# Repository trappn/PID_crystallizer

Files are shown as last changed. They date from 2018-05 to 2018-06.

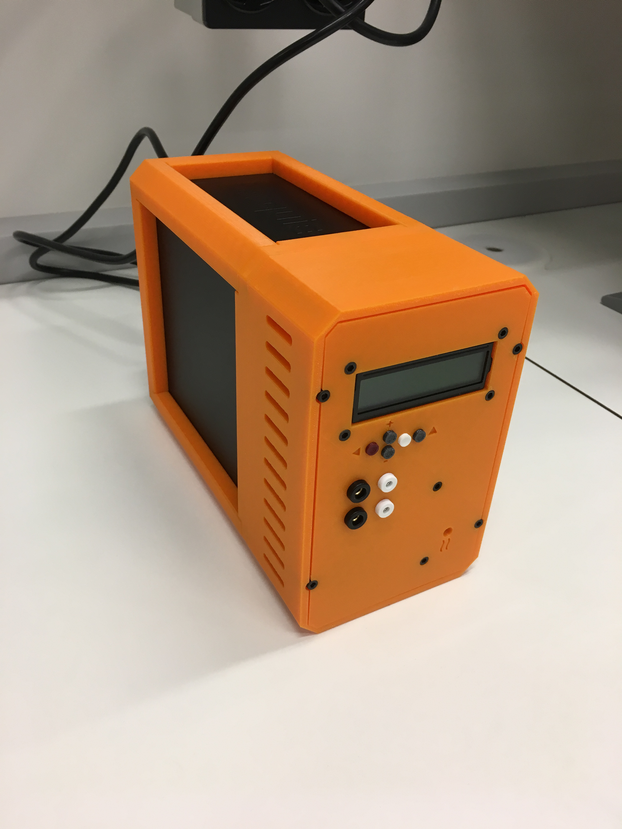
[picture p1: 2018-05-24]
photos/assembled_unit.JPG

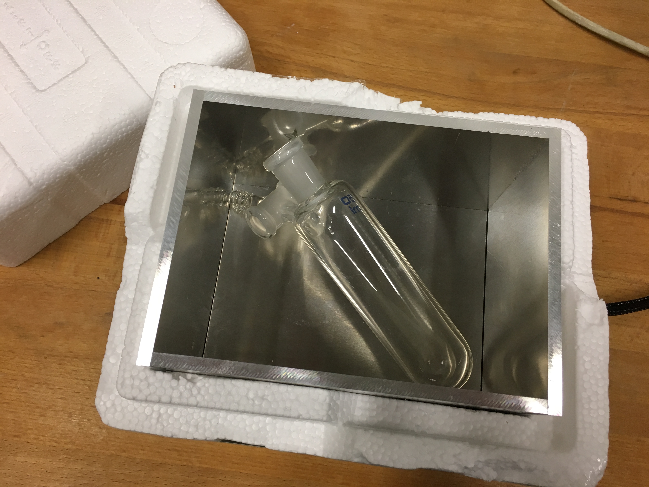
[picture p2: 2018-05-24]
photos/lowtemp_box_2.JPG

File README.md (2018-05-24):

# PID_crystallizer
Arduino-based programmable ramping PID controller 
<p>
Crystalheater Controller<br>
(c) N. Trapp @ Small Molecule Crystallography Center<br>
ETH Zürich, 2018<br>
</p>
<p>  
derived from:<br>
"Sous Vide Controller", (c) Bill Earl - for Adafruit Industries<br>
based on Arduino PID and PID AutoTune Libs, (c) Brett Beauregard<br>
</p>
<p>
 Used libraries: PID_v1.h, PID_AutoTune_v0.h, Wire.h, Adafruit_RGBLCDShield.h, SmoothThermistor.h, EEPROM.h
</p>
<p>
<ul>
  <li>designed around Arduino Uno with Robotdyn RGB 16x2 keypad shield, 100K NTC thermistor, standard DC/DC SSD and any 12V DC heating element</li>
  <li>minimized assembly time with ATX PSU & 3D printed case</li>
  <li>4 profiles for ramping (linear, oscillate, steps, sawtooth)</li>
  <li>uses PID autotuning (only necessary once for a specific heater setup) or manually set PID parameters</li>
  <li>can heat or cool</li>
  <li>logging via USB serial</li>
  <li>external wire harness allows placing heater box in fridge for cooling below RT</li>
  <li>stores settings in EEPROM</li>
  <li>projected runtime is displayed when changing settings</li>
  <li>thermistor safety: switches off when sensor shorts, breaks or is unplugged</li>
  <li>make sure to adjust Tmax (default:60) & Tmin (default:-40) in the sketch to safe values for your heater setup before compiling!</li>
  <li>extensive testing has shown long-term stability (>2 weeks) and accuracy (+/-0.1°C)</li>
</ul>
</p>

Usage:<br>
<table style="">
  
  <tr>
   <td>right</td><td>start or next</td>
  </tr>
  <tr>   
   <td>left</td><td>stop or previous, during ramping: stop and hold current temp</td>
  </tr>
  <tr>
   <td>up/down</td><td>during ramping&heating: show info screens</td>
  </tr>
  <tr>
   <td>shift</td><td>hold for larger increments in settings</td>
  </tr>
  <tr>
   <td>shift & +</td><td>start autotune (temp must be within 1°C of setpoint)</td>
  </tr>
  <tr>
   <td>shift & -</td><td>PID parameter settings</td>
  </tr>
  <tr>
   <td>shift & right</td><td>start ramp</td>
  </tr>
</table>

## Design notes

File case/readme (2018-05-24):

USBcover.scad contains only a simple plug (I drilled a 28mm hole in the case side to access the USB port for logging).

case structural parts (credits to alebrescia): https://www.thingiverse.com/thing:2321751
case faceplate & buttons: https://www.thingiverse.com/thing:2791368
heater box mold: https://www.thingiverse.com/thing:2891015
vial holders: https://www.thingiverse.com/thing:2891050

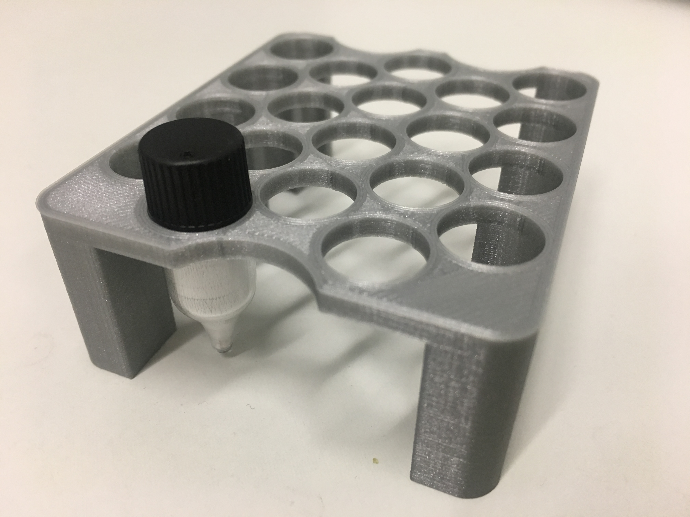
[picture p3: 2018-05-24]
photos/vialholder_small.JPG

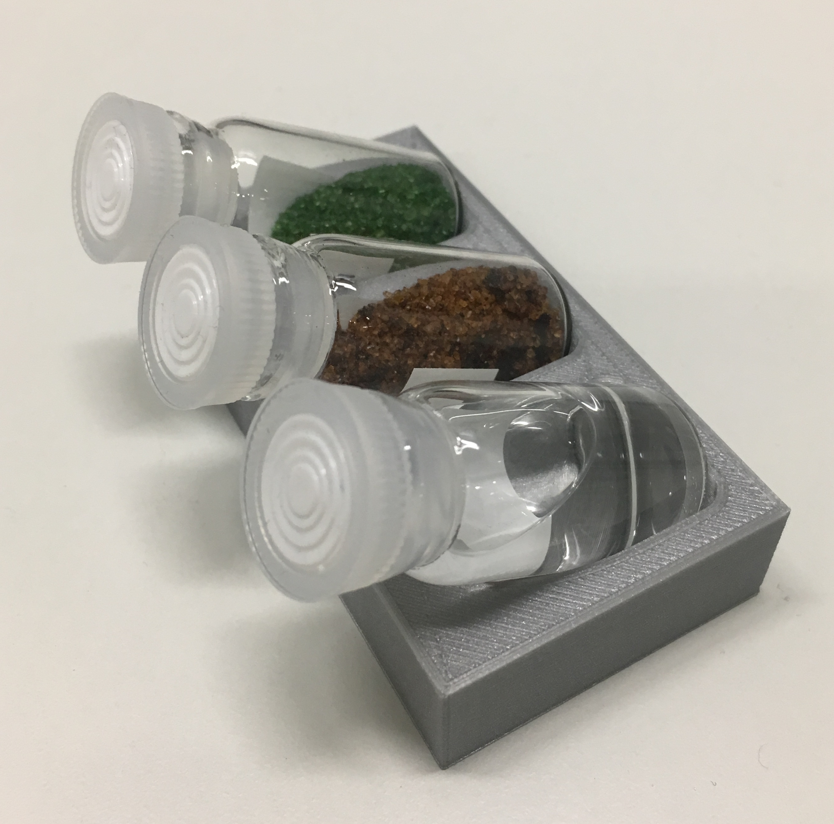
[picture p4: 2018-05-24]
photos/vialholder_large.JPG

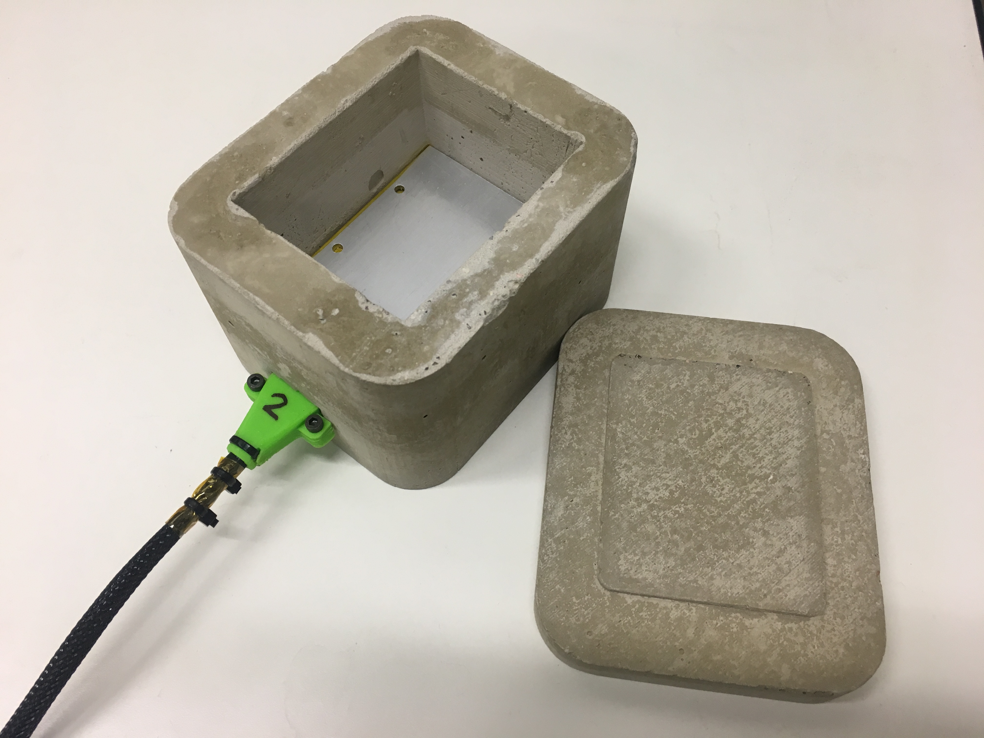
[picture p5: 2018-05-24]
photos/hightemp_box.JPG

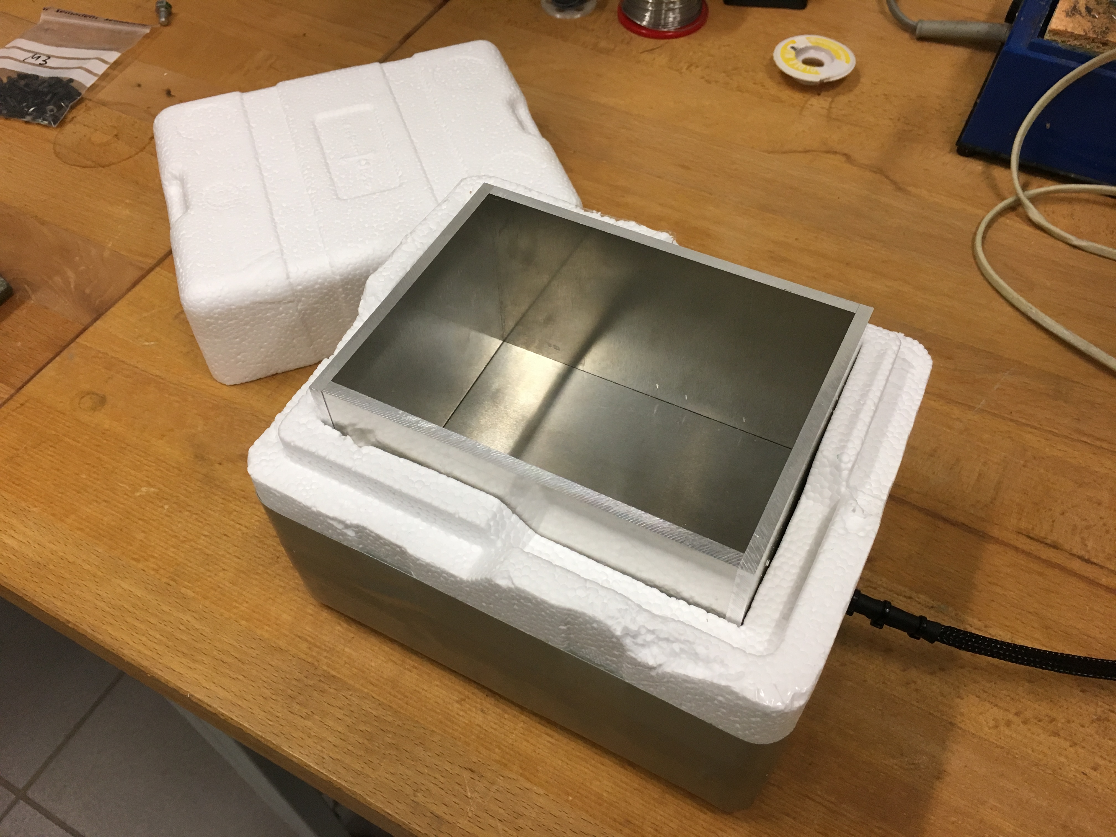
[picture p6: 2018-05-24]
photos/lowtemp_box_1.JPG

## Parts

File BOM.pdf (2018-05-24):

Part | Source (example) Link / Order No. (example) | Pack Unit Price (CHF) needed (# or m) Price total (CHF)

Electronics
ATX Power Supply >200W | scrap | | 1 | 0 | 1 | 0.00
Arduino UNO R3 clone | Aliexpress | https://www.aliexpress.com/item/high-quality-One-set-UNO-R3-MEGA328P-CH340G-For-Arduino-UNO-R3-Original-Chip-16Mhz/32833268761.html | 1 | 3.26 | 1 | 3.26
RGB LCD Shield with Keypad | Aliexpress | https://www.aliexpress.com/item/LCD-RGB-16x2-keypad-Buzzer-Shield-for-Arduino-LCD-RGB-1602/32812502875.html | 1 | 11.18 | 1 | 11.18
Solid State Relay DC-DC | Aliexpress | https://www.aliexpress.com/item/IMC-hot-New-Plastic-Metal-Solid-State-Relay-SSR-DC-DC-25A-3-32VDC-5-60VDC/32798514191.html | 1 | 4.07 | 1 | 4.07
Wires
Resistor 100kOhm | Aliexpress | https://www.aliexpress.com/item/100pcs-1-4W-1R-2-2M-1-Metal-film-resistor-series-100R-220R-1K-1-5K/32847096736.html | 100 | 0.66 | 1 | 0.01
Lab Jack Socket 2mm | | | | | 2
Lab Jack Socket 4mm | | | | | 2

Heater
Heater Element | | https://www.aliexpress.com/item/1PCS-PTC-Thermostat-Aluminum-Heating-Element-Heater-Plate-60W-AC-DC-12V-180-Degree-Incubator-Dehumidification/32812440130.html | 1 | 4.81 | 1 | 4.81
NTC Thermistor (100K, long wire) | Aliexpress | https://www.aliexpress.com/item/5Pcs-lot-100K-ohm-NTC-3950-Thermistors-with-cable-for-3D-Printer-Reprap-Mend-Free-Shipping/32642274542.html | 5 | 3.12 | 1 | 0.62
Power wire
Cable Sleeve | Aliexpress | https://www.aliexpress.com/item/Blue-Black-Insulation-Braided-Sleeving-4-6-8-10-12-15-20-25mm-Tight-PET-Expandable/32824518015.html | 5 | 3.82 | 2 | 1.53
Lab Jack 2mm | | | 1 | 1.04 | 2 | 2.08
Lab Jack 4mm | | | 1 | 1.19 | 2 | 2.38

Case
| | | 1 | | 1
Front Face & Buttons (3D printed) | Thingiverse | https://www.thingiverse.com/thing:2791368 | 1 | | 1
Case Frame (3D printed) | Thingiverse | https://www.thingiverse.com/thing:2321751 (only parts 1,2,3,4,6) | 1 | | 1
M3 cylinder head screws | | M3x10 (~10), M3x16 (~10), M3x20 (~20), M3x30(2)
M3 hex nuts | | | | | ~10

Consumables
Kapton Insulation Tape | Aliexpress | https://www.aliexpress.com/item/20mm-33M-100ft-Kapton-Tape-Adhesive-insulation-Resistant-Polyimide/32807829296.html
Solder
Heatshrink (various diameters)
| | | | | Sum: | 29.94

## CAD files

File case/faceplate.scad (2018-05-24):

$fn=60;

module blank() {
difference() {
  cube([81.5,61,4]);
  // window:
  translate([5.6,23,-0.5])  cube([71,24.8,5]);
  // buttons:
  translate([16.7,9.3,-0.5])  cylinder(h=5,d=6);
  translate([24.9,13.2,-0.5])  cylinder(h=5,d=6); 
  translate([24.9,5.4,-0.5])  cylinder(h=5,d=6); 
  translate([32.9,9.3,-0.5])  cylinder(h=5,d=6); 
  translate([40.7,9.3,-0.5])  cylinder(h=5,d=6);
  // M3 screws:
  translate([3,19.75,-0.5])  cylinder(h=5,d=3.5); 
  translate([3,50.75,-0.5])  cylinder(h=5,d=3.5); 
  translate([78.5,19.75,-0.5])  cylinder(h=5,d=3.5); 
  translate([78.5,50.75,-0.5])  cylinder(h=5,d=3.5);    
}
}

module button() {
color("green") {
difference() {
  union() {
    cylinder(h=7.5,d=5.6);
    cylinder(h=1,d=6.6);  
  }
 translate([0,0,-1])  cylinder(h=6,d=3.6);
 translate([0,0,12])  sphere(d=10);
}
}
}

module button_short() {
color("red") {
difference() {
  union() {
    cylinder(h=6.5,d=5.6);
    cylinder(h=1,d=6.6);  
  }
 translate([0,0,-1])  cylinder(h=6,d=3.6);
 translate([0,0,11])  sphere(d=10);
}
}
}

module front() {
// main (fits https://www.thingiverse.com/thing:2321751) 
translate([-8.85,-90.9,0])  {
difference() {
  cube([98.8,161.6,4]);
  // corners:
  translate([-3.5,-20,-1])  rotate([0,0,45])  cube([20,20,6]);
  translate([102.2,-20,-1])  rotate([0,0,45])  cube([20,20,6]);
  translate([-3.5,153.2,-1])  rotate([0,0,45])  cube([20,20,6]);
  translate([102.2,153.2,-1])  rotate([0,0,45])  cube([20,20,6]);
  // M3 through holes:
  translate([0.9,30.9,-0.5])  cylinder(h=10,d=3.4);
  translate([97.9,30.9,-0.5])  cylinder(h=10,d=3.4);
  translate([0.9,131.9,-0.5])  cylinder(h=10,d=3.4);
  translate([97.9,131.9,-0.5])  cylinder(h=10,d=3.4);
  // sink holes:
  translate([0.9,30.9,1])  cylinder(h=10,d=5.7);
  translate([97.9,30.9,1])  cylinder(h=10,d=5.7);
  translate([0.9,131.9,1])  cylinder(h=10,d=5.7);
  translate([97.9,131.9,1])  cylinder(h=10,d=5.7);
  // Thermistor sockets:
  translate([35,80,-1])  cylinder(h=10,d=6.5);
  translate([35,65,-1])  cylinder(h=10,d=6.5);
  // Heater power sockets:
  translate([20,80,-1])  cylinder(h=10,d=8.5);
  translate([20,65,-1])  cylinder(h=10,d=8.5);
  // SSR LED window:
  translate([77.9,32.9,-0.1])  cylinder(h=4.2,d1=3,d2=6);
  // SSR fixings + sink holes (M3):
  translate([65.9,17.9,-1])  cylinder(h=10,d=3.5);
  translate([65.9,65.9,-1])  cylinder(h=10,d=3.5);
  translate([65.9,17.9,1])  cylinder(h=10,d=5.7);
  translate([65.9,65.9,1])  cylinder(h=10,d=5.7);
  // USB socket + sink holes (M3):
  //translate([71.6,80,0]) {
  //rotate([0,0,90]) {
  //  translate([0,0,0])  cube([9,10,10],center=true);
  //  translate([0,0,4])  cube([15,16,4],center=true);
  //  translate([0,15,-1])  cylinder(d=3.5,h=10);  
  //  translate([0,-15,-1])  cylinder(d=3.5,h=10);
  //  translate([0,15,2])  cylinder(d=5.7,h=10);  
  //  translate([0,-15,2])  cylinder(d=5.7,h=10);
  //}
  //}
  // TEXT:
  // shift:
  translate([57.5,99.6,3])  linear_extrude(height=2)  text("", font = "Wingdings3", size=6,halign="center",valign="center");
  // back:
  translate([18,100.2,3])  linear_extrude(height=2)  text("", font = "Wingdings3", size=4,halign="center",valign="center");
  // + and -
  translate([33.75,110,3])  linear_extrude(height=2)  text("+", font = "Liberation Sans:style=Bold", size=6,halign="center",valign="center");
  translate([33.75,90,3])  linear_extrude(height=2)  text("-", font = "Liberation Sans:style=Bold", size=6,halign="center",valign="center");
  // heater active symbol:
  translate([79.2,24,3])  rotate([0,0,90])  linear_extrude(height=2)  text("≈", size=12,halign="center",valign="center");
  // DISPLAY:
  translate([8.85,90.9,0])  {
    // display window:
    translate([5.6,23,-0.5])  cube([71,24.8,5]);
    // display buttons:
    translate([16.7,9.3,-0.5])  cylinder(h=5,d=6);
    translate([24.9,13.2,-0.5])  cylinder(h=5,d=6); 
    translate([24.9,5.4,-0.5])  cylinder(h=5,d=6); 
    translate([32.9,9.3,-0.5])  cylinder(h=5,d=6); 
    translate([40.7,9.3,-0.5])  cylinder(h=5,d=6);
    // display M3 screws:
    translate([3,19.75,-0.5])  cylinder(h=5,d=3.5); 
    translate([3,50.75,-0.5])  cylinder(h=5,d=3.5); 
    translate([78.5,19.75,-0.5])  cylinder(h=5,d=3.5); 
    translate([78.5,50.75,-0.5])  cylinder(h=5,d=3.5);
    // display M3 sink holes:
    translate([3,19.75,1])  cylinder(h=5,d=5.7); 
    translate([3,50.75,1])  cylinder(h=5,d=5.7); 
    translate([78.5,19.75,1])  cylinder(h=5,d=5.7); 
    translate([78.5,50.75,1])  cylinder(h=5,d=5.7);
  }   
}
}
}

// SSR:
//translate([35,-80,-24])  cube([44,60,25]);

//color("red",0.3) translate([0,0,1]) blank();

//translate([16.7,9.3,-0.5])  button();
//translate([24.9,13.2,-0.5])  button();
//translate([24.9,5.4,-0.5])  button();
//translate([32.9,9.3,-0.5])  button();
//translate([40.7,9.3,-0.5])  button();
front();
//button();
//translate([0,10,0])  button_short();

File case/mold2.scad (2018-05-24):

$fn=50;
use <scad_libs//cyl_head_bolt.scad>

module fillet(r, h) {
// generates rounded corners
    translate([r / 2, r / 2, 0])
        difference() {
            cube([r + 0.01, r + 0.01, h], center = true);
            translate([r/2, r/2, 0])
                cylinder(r = r, h = h + 1, center = true);
        }
}

module dummy() {
color("silver") {
  translate([0,8.5,0])  cube([76,45,4.5]); 
  difference() {
    translate([0,0,4.5])  cube([76,62,2]); 
    translate([22,5,-1])  cylinder(h=10, d=3.5);
    translate([54,5,-1])  cylinder(h=10, d=3.5);
    translate([22,57,-1])  cylinder(h=10, d=3.5);
    translate([54,57,-1])  cylinder(h=10, d=3.5);
  }    
  translate([0,24,2.5])  rotate([0,90,180])  cylinder(h=12, d=3.8);
  translate([0,39,2.5])  rotate([0,90,180])  cylinder(h=12, d=3.8);
}
}

module positive() {
  difference() {
    translate([-22,-19,-23])  cube([120,100,80]);
    // rounded corners:
    translate([-22,-19,20])  rotate([0,0,0])  fillet(20,100);
    translate([-22,81,20])  rotate([0,0,270])  fillet(20,100);
    translate([98,-19,20])  rotate([0,0,90])  fillet(20,100);
    translate([98,81,20])  rotate([0,0,180])  fillet(20,100);
    // cable hole:
    translate([-22.1,21.4,-5.5])  cube([40,20.2,10.2]);  
    // lower recess:
    translate([0,8,-8])  cube([78,46,25]);
    // upper recess: 
    hull() {
      translate([0,-0.5,4.5])  cube([78,63,1]); 
      translate([-2,-2.5,57])  cube([82,67,1]); 
    }
  }
}

module mold_inner(d=1) {
  difference() {
    translate([0,8,-8])  cube([78,46,25]);
    // socket for teflon spacer 40*20*10:
    translate([-22,21.4,-5.5])  cube([40,20.2,10.2]);
  }
    translate([-2,-2.5,57])  cube([82,67,5]);
    translate([-24-d,21.5,60])  cube([124+2*d,20,2]);
    translate([28,-21-d,60])  cube([20,104+2*d,2]);
    // spacers:
    translate([-22-d,21.5,57])  cube([d,20,3]);
    translate([98,21.5,57])  cube([d,20,3]);
    translate([28,-19-d,57])  cube([20,d,3]);
    translate([28,81,57])  cube([20,d,3]);
    //downward clips:
    translate([-24-d,21.5,52])  cube([2,20,8]);
    translate([98+d,21.5,52])  cube([2,20,8]);
    translate([28,-21-d,52])  cube([20,2,8]);
    translate([28,81+d,52])  cube([20,2,8]);
    hull() {
      translate([0,-0.5,4.5])  cube([78,63,1]); 
      translate([-2,-2.5,57])  cube([82,67,1]);
    }
}

module mold_outer(d=1) {
color("blue",0.3) {
  difference() {
    translate([-22-d,-19-d,-23-d])  cube([120+2*d,100+2*d,80+d]); 
    difference() {
      translate([-22,-19,-23])  cube([120,100,81]);
      translate([-22,-19,20])  rotate([0,0,0])  fillet(20,100);
      translate([-22,81,20])  rotate([0,0,270])  fillet(20,100);
      translate([98,-19,20])  rotate([0,0,90])  fillet(20,100);
      translate([98,81,20])  rotate([0,0,180])  fillet(20,100); 
    }
    translate([-22-d,-19-d,20])  rotate([0,0,0])  fillet(20,100);
    translate([-22-d,81+d,20])  rotate([0,0,270])  fillet(20,100);
    translate([98+d,-19-d,20])  rotate([0,0,90])  fillet(20,100);
    translate([98+d,81+d,20])  rotate([0,0,180])  fillet(20,100); 
  }
}
}

module strain_relief1() {
color("red") {
  difference() {
    union() {
      translate([-30,15.5,-5.4])  cube([7.5,32,5]);  
      hull() {
        translate([-22,21.5,-5.4])  cube([13,20,5]);
        difference() {
          translate([-48,31.5,-0.4])  rotate([0,90,0])  cylinder(d=10,h=1);
          translate([-50,21.5,-0.4])  cube([5,20,10]);
        }
      }
    }    
    translate([-13,31.5,-30])  cylinder(h=100,d=3.5);  
    translate([-13,31.5,0.2])  nutcatch_parallel("M3");
    translate([-26,19,-1.4])  nutcatch_parallel("M3");
    translate([-26,44,-1.4])  nutcatch_parallel("M3");
    translate([-26,19,-5])  cylinder(d=3.5,h=10);
    translate([-26,44,-5])  cylinder(d=3.5,h=10);
    translate([-30.1,15.4,-5])  rotate([0,0,0])  fillet(3,100);
    translate([-30.1,47.6,-5])  rotate([0,0,270])  fillet(3,100);
    translate([-46,26.5,-10])  cube([4,1,20]);
    translate([-46,35.5,-10])  cube([4,1,20]); 
    translate([-51,31.5,-0.4])  rotate([0,90,0])  cylinder(d=6.5,h=12);
    hull() {
      translate([-40,31.5,-0.4])  rotate([0,90,0])  cylinder(d=6.5,h=1);
      translate([-9,31.5,-0.4])  rotate([0,90,0])  scale([1,3.5,1])  cylinder(d=5,h=1);
    }
  }
}
}

module strain_relief2() {
color("red") {
  difference() {
    union() {
      translate([-30,15.5,-0.4])  cube([7.5,32,2]);  
      hull() {
        translate([-22,21.5,-0.4])  cube([4,20,4.5]);
        difference() {
          translate([-48,31.5,-0.4])  rotate([0,90,0])  cylinder(d=10,h=1);
          translate([-50,21.5,-10.4])  cube([5,20,10]);
        }
      }
    }    
    translate([-26,19,-1.4])  nutcatch_parallel("M3");
    translate([-26,44,-1.4])  nutcatch_parallel("M3");
    translate([-26,19,-5])  cylinder(d=3.5,h=10);
    translate([-26,44,-5])  cylinder(d=3.5,h=10);
    translate([-30.1,15.4,-5])  rotate([0,0,0])  fillet(3,100);
    translate([-30.1,47.6,-5])  rotate([0,0,270])  fillet(3,100);
    translate([-46,26.5,-10])  cube([4,1,20]);
    translate([-46,35.5,-10])  cube([4,1,20]); 
    translate([-51,31.5,-0.4])  rotate([0,90,0])  cylinder(d=6.5,h=12);
    hull() {
      translate([-40,31.5,-0.4])  rotate([0,90,0])  cylinder(d=6.5,h=1);
      translate([-9,31.5,-0.4])  rotate([0,90,0])  scale([1,3.5,1])  cylinder(d=5,h=1);
    }
  }
}
}

module drill_jig() {
color("blue") {
  difference() {
    translate([-23.5,21.7,-24])  cube([15,19.6,19.5]);     
    translate([-22,21,-23])  cube([14,22,18]);
    translate([-13,31.5,-30])  cylinder(h=10,d=3.5);       
  }
}
}

module vialholder() {
color("orange") {
  difference() {
    translate([-14,-33,-10])  cube([76,40,15]);
    hull() {
      translate([0,0,0])  rotate([60,0,0])  cylinder(d=19,h=45);
      translate([0,0,30])  rotate([60,0,0])  cylinder(d=19,h=45);
    }
    hull() {
      translate([24,0,0])  rotate([60,0,0])  cylinder(d=19,h=45);
      translate([24,0,30])  rotate([60,0,0])  cylinder(d=19,h=45);
    }
    hull() {
      translate([48,0,0])  rotate([60,0,0])  cylinder(d=19,h=45);
      translate([48,0,30])  rotate([60,0,0])  cylinder(d=19,h=45);
    }
  }
}
}

module lidpositive() {
color("lightgrey") {
  difference() {
    translate([-1,-1.5,57.1])  cube([80,65,3]);
    translate([-1.1,-1.6,56])  rotate([0,0,0])  fillet(5,10);
    translate([-1.1,63.6,56])  rotate([0,0,270])  fillet(5,10);
    translate([79.1,-1.6,56])  rotate([0,0,90])  fillet(5,10);
    translate([79.1,63.6,56])  rotate([0,0,180])  fillet(5,10); 
  }
  difference() {
    translate([-22,-19,60])  cube([120,100,20]);
    // rounded corners:
    translate([-22,-19,70])  rotate([0,0,0])  fillet(20,50);
    translate([-22,81,70])  rotate([0,0,270])  fillet(20,50);
    translate([98,-19,70])  rotate([0,0,90])  fillet(20,50);
    translate([98,81,70])  rotate([0,0,180])  fillet(20,50);
  }
}
}

module lidmold(d=1) {
color("lightgrey") {
difference() {
  translate([-22-d,-19-d,57.1-d])  cube([120+2*d,100+2*d,27+d]);
  difference() {
    translate([-1,-1.5,57.1])  cube([80,65,3]);
    translate([-1.1,-1.6,56])  rotate([0,0,0])  fillet(5,10);
    translate([-1.1,63.6,56])  rotate([0,0,270])  fillet(5,10);
    translate([79.1,-1.6,56])  rotate([0,0,90])  fillet(5,10);
    translate([79.1,63.6,56])  rotate([0,0,180])  fillet(5,10); 
  }
  difference() {
    translate([-22,-19,60])  cube([120,100,25]);
    // rounded corners:
    translate([-22,-19,70])  rotate([0,0,0])  fillet(20,50);
    translate([-22,81,70])  rotate([0,0,270])  fillet(20,50);
    translate([98,-19,70])  rotate([0,0,90])  fillet(20,50);
    translate([98,81,70])  rotate([0,0,180])  fillet(20,50);
  }
}
}
}

module carrier() {
  difference() {
    translate([0,0,0])  cube([70,60,26]);
    translate([-1,10,3])  cube([72,40,26]);
    translate([-0.1,-0.1,10])  rotate([0,0,0])  fillet(5,60);
    translate([-0.1,60.1,10])  rotate([0,0,270])  fillet(5,60);
    translate([70.1,-0.1,10])  rotate([0,0,90])  fillet(5,60);
    translate([70.1,60.1,10])  rotate([0,0,180])  fillet(5,60);
    translate([75,30,-1])  cylinder(d=20,h=50);
    translate([-5,41,-1])  cylinder(d=20,h=50);
    translate([-5,18.5,-1])  cylinder(d=20,h=50);
    for (x = [0:3])
       for (y = [0:2])
          translate([15*x+8.5,22.5*y+7.5,-1])  cylinder(d=12,h=50);
    for (x = [0:3])
       for (y = [0:1])
          translate([15*x+16,22.5*y+18.5,-1])  cylinder(d=12,h=50);    
     
  }
}

carrier();
//dummy();
//positive();
//mold_inner(1);
//mold_outer(1); 
//strain_relief1();
//strain_relief2();
//translate([-20,0,0])  drill_jig();
//translate([14,50,23])  vialholder();
//lidpositive();
//lidmold(); 

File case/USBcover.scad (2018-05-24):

$fn=80;
difference() {
  union() {
    cylinder(h=1,d=30);
    translate([0,0,1]) cylinder(h=6,d=28.2);
    translate([0,0,7]) cylinder(h=1,d1=28.2,d2=27);
  }
  translate([0,0,6])  cube([30,10,10],center=true);
}

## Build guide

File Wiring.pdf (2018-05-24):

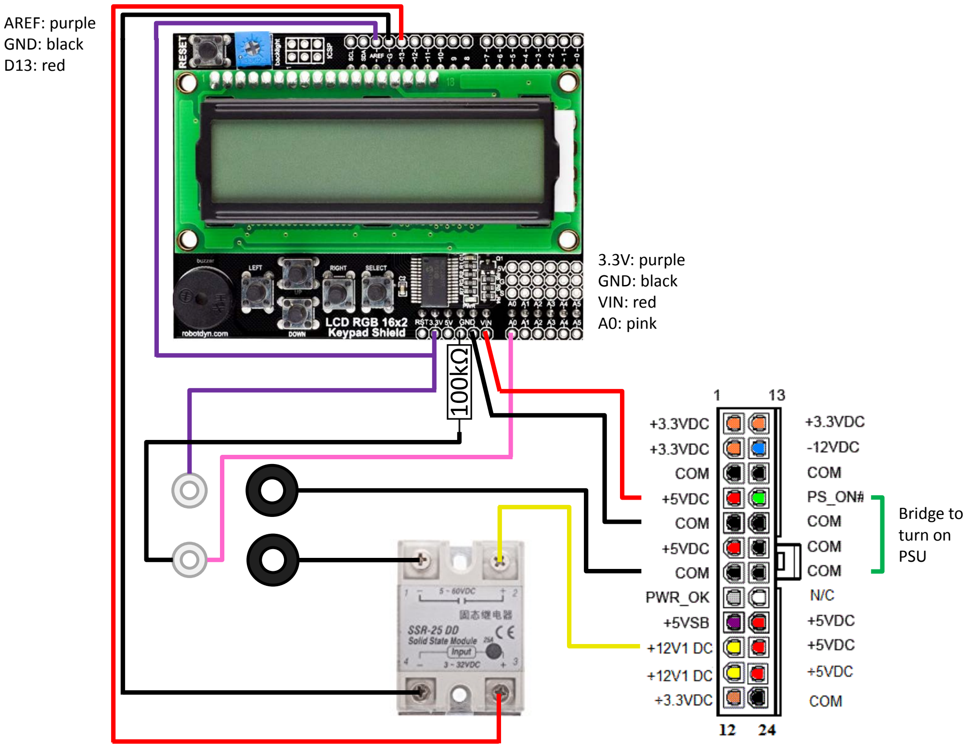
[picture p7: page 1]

100kΩ

AREF: purple
GND: black
D13: red

3.3V: purple
GND: black
VIN: red
A0: pink

Bridge to
turn on
PSU

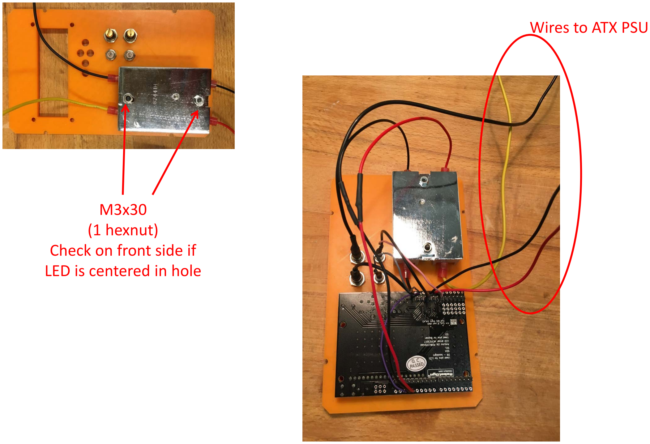
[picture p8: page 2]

Wires to ATX PSU

M3x30
(1 hexnut)
Check on front side if
LED is centered in hole

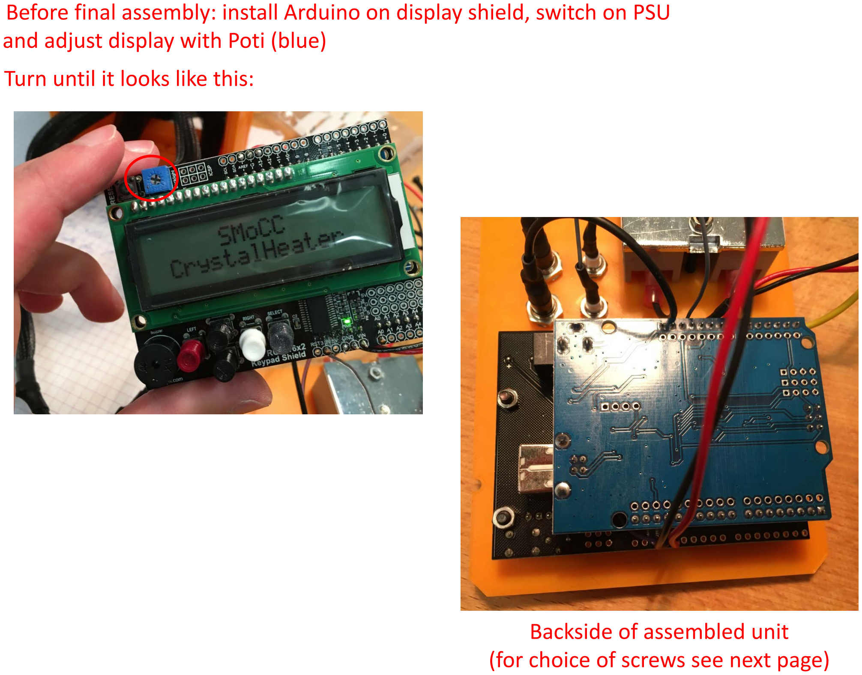
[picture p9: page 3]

Before final assembly: install Arduino on display shield, switch on PSU and adjust display with Poti (blue)
Turn until it looks like this:

Backside of assembled unit (for choice of screws see next page)

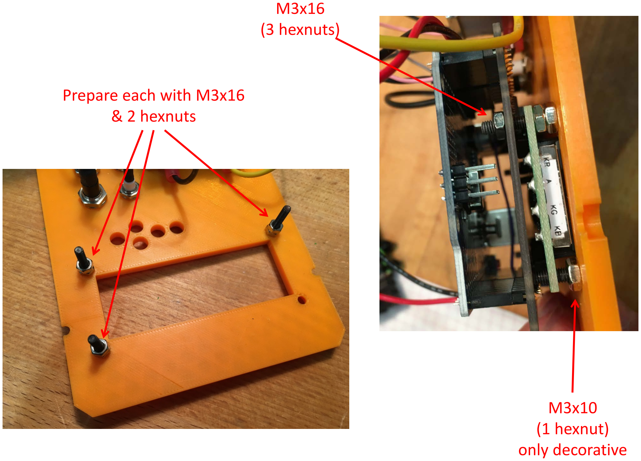
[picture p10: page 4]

M3x10
(1 hexnut)
only decorative

M3x16
(3 hexnuts)

Prepare each with M3x16
& 2 hexnuts

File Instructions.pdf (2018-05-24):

General Usage:
- Start / Cycle Options
- Stop / Cycle Options
-------------------------------------------Hold/Heat Mode:
- Settings
- & Start Ramp
- & Tune PID Params
(within 1°C of Setpoint:
- & Start Auto-Tune)
-------------------------------------------While Ramping:
- Stop & Hold
- / Show Info Screens
-------------------------------------------In Settings Screens:
- Increase
- & Increase fast
- Decrease
- & Decrease fast

Firmware Tmin: Tmax:

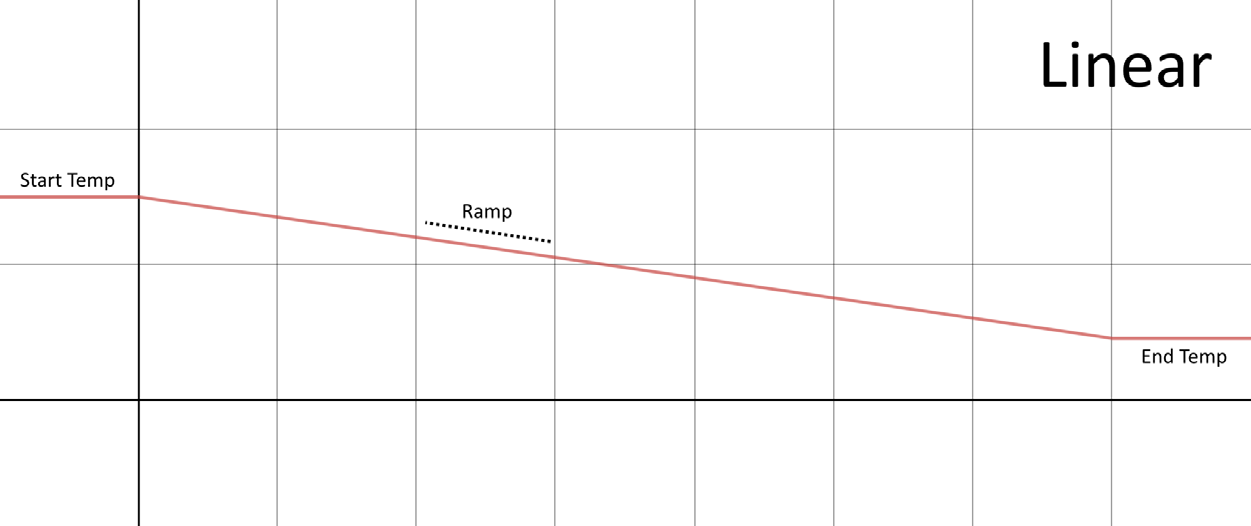
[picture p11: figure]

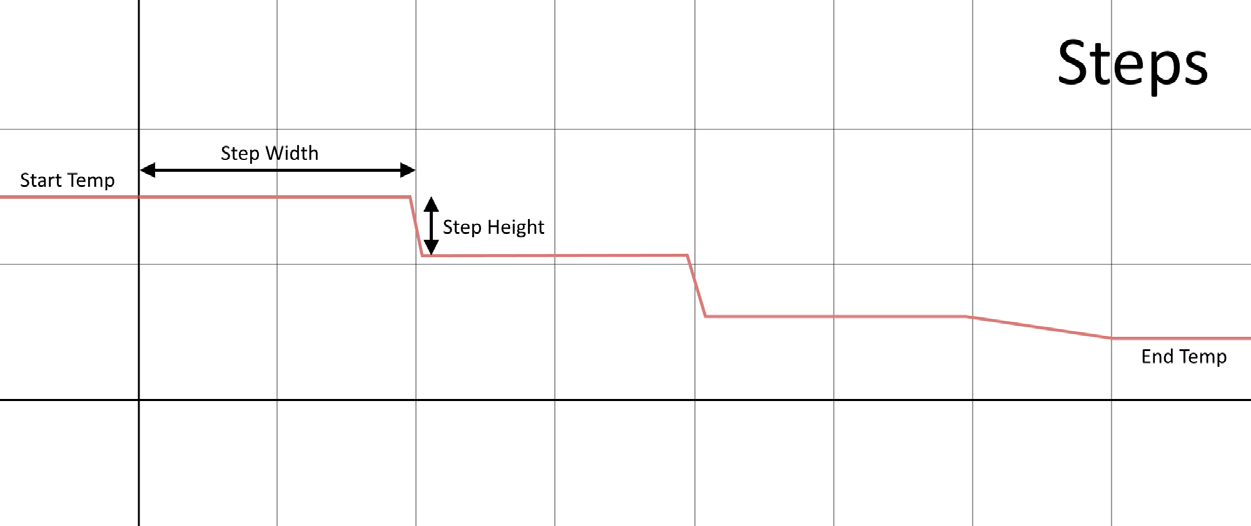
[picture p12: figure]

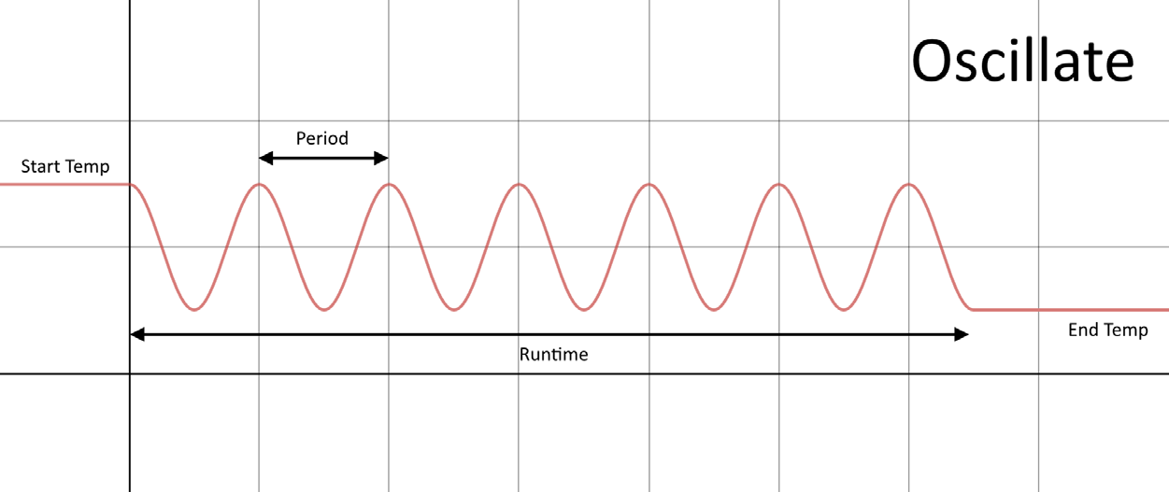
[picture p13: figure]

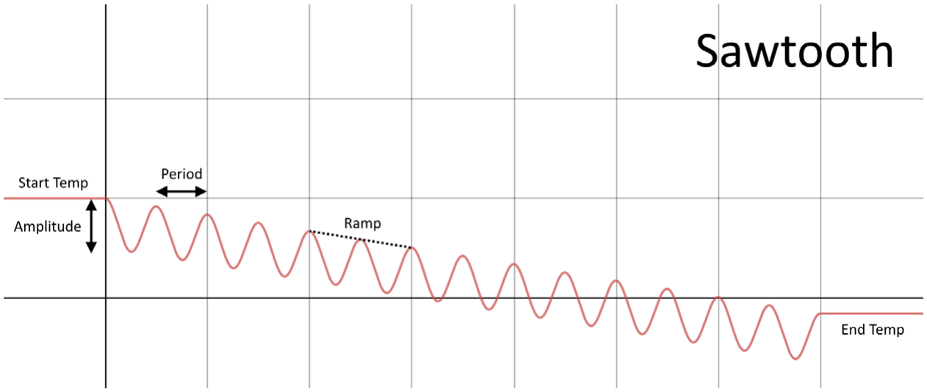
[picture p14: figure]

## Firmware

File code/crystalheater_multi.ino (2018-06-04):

//-------------------------------------------------------------------
// Crystalheater Controller
// (c) N. Trapp @ Small Molecule Crystallography Center
// ETH Zürich, 2018
//
// derived from:
// "Sous Vide Controller", (c) Bill Earl - for Adafruit Industries
// based on Arduino PID and PID AutoTune Libs, (c) Brett Beauregard
// Usage:
//        right         : start or next
//        left          : stop or previous,
//                        during ramping: stop and hold current temp
//        up/down       : during ramping&heating: show info screens
//        shift         : hold for larger increments in settings
//        shift & +     : start autotune (temp must be within 1°C
//                        of setpoint)
//        shift & -     : PID parameter settings
//        shift & right : start ramp
//
// Log format: Current T(°C), Setpoint(°C), Power(%), Runtime(min)
//------------------------------------------------------------------

// PID Library
#include <PID_v1.h>
#include <PID_AutoTune_v0.h>

// Libraries for the Adafruit RGB/LCD Shield
#include <Wire.h>
#include <Adafruit_RGBLCDShield.h>

// include the SmoothThermistor library
#include <SmoothThermistor.h>

// So we can save and retrieve settings
#include <EEPROM.h>

// ************************************************
// Pin definitions
// ************************************************

// Output for SSR DC/DC Relay
#define RelayPin 13

// Output Beeper (Sensor Errors and Ramp finished)
#define BuzzerPin 2

// ************************************************
// PID Variables and constants
// ************************************************

//Min&Max Temps/Ramps:
const int Tmax = 60;
const int Tmin = -40;
const double Rmax = 20.0;
const double Rmin = 0.05;  // also sets the ramp increment
const float Pi = 3.14159;

//Define Variables we'll be connecting to
double Setpoint;
double Ramprate;
double Endpoint;
double Timescale;
double Oruntime;
double Operiod;
double Oamp;
int Swdt;
double Shgh;
double Input;
double Output;
unsigned long Starttime;
double Starttemp;
double Rrmillis;
int Modei;
int Nsteps;
char *Modes[] = { "LINEAR", "STEPS", "OSCILLATE", "SAWTOOTH"};
char buffer[10]; // BUFFER FOR FORMATTING OUTPUT

volatile long onTime = 0;

// pid tuning parameters
double Kp;
double Ki;
double Kd;

// EEPROM addresses for persisted data
const int SpAddress = 0;
const int KpAddress = 8;
const int KiAddress = 16;
const int KdAddress = 24;
const int EpAddress = 32;
const int RrAddress = 40;
const int MdAddress = 48;
const int OrAddress = 56;
const int OpAddress = 64;
const int OaAddress = 72;
const int SwAddress = 80;
const int ShAddress = 88;

//Specify the links and initial tuning parameters
PID myPID(&Input, &Output, &Setpoint, Kp, Ki, Kd, DIRECT);

// 1 second Time Proportional Output window
int WindowSize = 1000; 
unsigned long windowStartTime;

// ************************************************
// Auto Tune Variables and constants
// ************************************************
byte ATuneModeRemember=2;

double aTuneStep=500;
double aTuneNoise=1;
unsigned int aTuneLookBack=20;

boolean tuning = false;

PID_ATune aTune(&Input, &Output);

// ************************************************
// Display Variables and constants
// ************************************************

Adafruit_RGBLCDShield lcd = Adafruit_RGBLCDShield();
// These #defines make it easy to set the backlight color
#define RED 0x1
#define YELLOW 0x3
#define GREEN 0x2
#define TEAL 0x6
#define BLUE 0x4
#define VIOLET 0x5
#define WHITE 0x7

#define BUTTON_SHIFT BUTTON_SELECT

unsigned long lastInput = 0; // last button press

byte degree[8] = // define the degree symbol 
{ 
 B00110, 
 B01001, 
 B01001, 
 B00110, 
 B00000,
 B00000, 
 B00000, 
 B00000 
}; 

unsigned long adjInterval; // ramp temp stepping
const long logInterval = 5000; // log every 5 seconds
unsigned long lastAdjTime = 0;
unsigned long lastLogTime = 0;

// ************************************************
// States for state machine
// ************************************************
enum operatingState { OFF = 0, SETM, SETP, SETOR, SETOA, SETOP, SETSW, SETSH, SETE, SETR, RUN, RMP, ERR, TUNE_P, TUNE_I, TUNE_D, AUTO};
operatingState opState = OFF;

// ************************************************
// Sensor Variables and constants
// Temp Data wire is plugged into port A0 on the Arduino

// create a SmoothThermistor instance, reading from analog pin 0
// using a common 100K NTC thermistor.
SmoothThermistor sensors(A0,ADC_SIZE_10_BIT,100000,100000);

// ************************************************
// Setup and display initial screen
// ************************************************
void setup()
{
   Serial.begin(9600);

   // Initialize Relay Control:

   pinMode(RelayPin, OUTPUT);    // Output mode to drive relay
   digitalWrite(RelayPin, LOW);  // make sure it is off to start

   // Thermistor setup:
   // use the AREF pin, so we can measure on 3.3v, which has less noise on an Arduino
   // make sure your thermistor is fed using 3.3v, along with the AREF pin
   // so the 3.3v output pin goes to the AREF pin and the thermistor
   // see "the advanced circuit" on top of this sketch
   sensors.useAREF(true);

   // Initialize LCD DiSplay 

   lcd.begin(16, 2);
   lcd.createChar(1, degree); // create degree symbol from the binary
   
   lcd.setBacklight(VIOLET);
   lcd.print(F("     SMoCC"));
   lcd.setCursor(0, 1);
   lcd.print(F(" CrystalHeater"));

//   if (!sensors.temperature()) 
//   {
//      lcd.setCursor(0, 1);
//      lcd.print(F("Sensor Error"));
//   }

   delay(3000);  // Splash screen

   // Initialize the PID and related variables
   LoadParameters();
   myPID.SetTunings(Kp,Ki,Kd);

   myPID.SetSampleTime(1000);
   myPID.SetOutputLimits(0, WindowSize);

  // Run timer2 interrupt every 15 ms 
  TCCR2A = 0;
  TCCR2B = 1<<CS22 | 1<<CS21 | 1<<CS20;

  //Timer2 Overflow Interrupt Enable
  TIMSK2 |= 1<<TOIE2;
}

// ************************************************
// Timer Interrupt Handler
// ************************************************
SIGNAL(TIMER2_OVF_vect) 
{
  if (opState == OFF)
  {
    digitalWrite(RelayPin, LOW);  // make sure relay is off
  }
  else
  {
    DriveOutput();
  }
}

// ************************************************
// Main Control Loop
//
// All state changes pass through here
// ************************************************
void loop()
{
   // wait for button release before changing state
   while(ReadButtons() != 0) {}

   lcd.clear();

   switch (opState)
   {
   case OFF:
      Off();
      break;
   case SETM:
      Tune_Md();
      break;
   case SETOR:
      Tune_Or();
      break;
   case SETOP:
      Tune_Op();
      break;
   case SETOA:
      Tune_Oa();
      break;     
   case SETP:
      Tune_Sp();
      break;
   case SETE:
      Tune_Ep();
      break;
   case SETR:
      Tune_Rr();
      break;
   case SETSW:
      Tune_Sw();
      break;
   case SETSH:
      Tune_Sh();
      break;
   case RUN:
      Run();
      break;
   case RMP:
      Ramp();
      break;
   case ERR:
      Error();
      break;
   case TUNE_P:
      TuneP();
      break;
   case TUNE_I:
      TuneI();
      break;
   case TUNE_D:
      TuneD();
      break;
   }
}

// ************************************************
// Initial State - press RIGHT to start heating
// ************************************************
void Off()
{
   myPID.SetMode(MANUAL);
   lcd.setBacklight(0);
   digitalWrite(RelayPin, LOW);  // make sure it is off
   lcd.print(F("     SMoCC"));
   lcd.setCursor(0, 1);
   lcd.print(F(" CrystalHeater"));
   uint8_t buttons = 0;
   
   while(!(buttons & (BUTTON_RIGHT)))
   {
      buttons = ReadButtons();
   }
   // Prepare to transition to the RUN state
   // turn the PID on:
   myPID.SetMode(AUTOMATIC);
   windowStartTime = millis();
   opState = RUN; // start control
}

// ************************************************
// Mode Entry State
// UP/DOWN to change ramp mode
// RIGHT to change Start Temp
// LEFT for Run mode
// SHIFT for 0.1x tuning
// ************************************************
void Tune_Md()
{
   lcd.setBacklight(VIOLET);
   lcd.print(F("Ramp Mode:"));
   uint8_t buttons = 0;
   while(true)
   {
      buttons = ReadButtons();

      if (buttons & BUTTON_LEFT)
      {
         opState = RUN;
         return;
      }
      if (buttons & BUTTON_RIGHT)
      {
         opState = SETP;
         return;
      }
      if (buttons & BUTTON_UP)
      {
         Modei += 1;
         delay(200);
      }
      if (buttons & BUTTON_DOWN)
      {
         Modei -= 1;
         Setpoint = int(Setpoint);
         delay(200);
      }
      if (Modei > 3)
      {
         Modei = 0;
      }
      else if (Modei < 0)
      {
         Modei = 3;         
      }
      else
      {
         if ((millis() - lastInput) > 10000)  // return to RUN after 10 seconds idle
         {
            opState = RUN;
            return;
         }
         
         lcd.setCursor(0,1);
         lcd.print(Modes[Modei]);
         lcd.print("      ");
         DoControl();
      }
   }
}

// ************************************************
// Setpoint / Start Temp Entry State
// UP/DOWN to change setpoint
// RIGHT for tuning parameters
// LEFT for set mode
// SHIFT for 0.1x tuning
// ************************************************
void Tune_Sp()
{
   lcd.setBacklight(VIOLET);
   lcd.print(F("Start Temp ["));
   lcd.write(1);
   lcd.print(F("C]:"));
   uint8_t buttons = 0;
   while(true)
   {
      buttons = ReadButtons();

      float increment = 1;
      if (buttons & BUTTON_SHIFT)
      {
        increment *= 10;
      }
      if (buttons & BUTTON_LEFT)
      {
         opState = SETM;
         return;
      }
      if (buttons & BUTTON_RIGHT)
      {
         opState = SETE;
         return;
      }
      if (buttons & BUTTON_UP)
      {
         Setpoint += increment;
         Setpoint = int(Setpoint);
         delay(200);
      }
      if (buttons & BUTTON_DOWN)
      {
         Setpoint -= increment;
         Setpoint = int(Setpoint);
         delay(200);
      }
      if (Setpoint > Tmax)
      {
         Setpoint = int(Tmin);
      }
      else if (Setpoint < Tmin)
      {
         Setpoint = int(Tmax);         
      }
      else
      {
         if ((millis() - lastInput) > 10000)  // return to RUN after 10 seconds idle
         {
            opState = RUN;
            return;
         }
      if (Modei == 1) // STEPS
      {
         // The weird multiplication is necessary to prevent typecasting errors...
         Nsteps = int((10*(abs(Setpoint - Endpoint)))/int(10*Shgh));
         Timescale = double(Nsteps*Swdt)/60;   
      }
      else
      {
         Timescale = (abs(Setpoint - Endpoint))/Ramprate;
      }   
         lcd.setCursor(0,1);
         lcd.print(int(Setpoint));
         lcd.print("   ");
         lcd.setCursor(10,1);
         if (Modei != 2)   // show runtime where it makes sense
         {
           lcd.print(Timescale,1);    
           lcd.print(F("h  "));
         }
         DoControl();
      }
   }
}
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
